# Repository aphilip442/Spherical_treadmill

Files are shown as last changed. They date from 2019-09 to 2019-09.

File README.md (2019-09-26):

# Spherical_treadmill

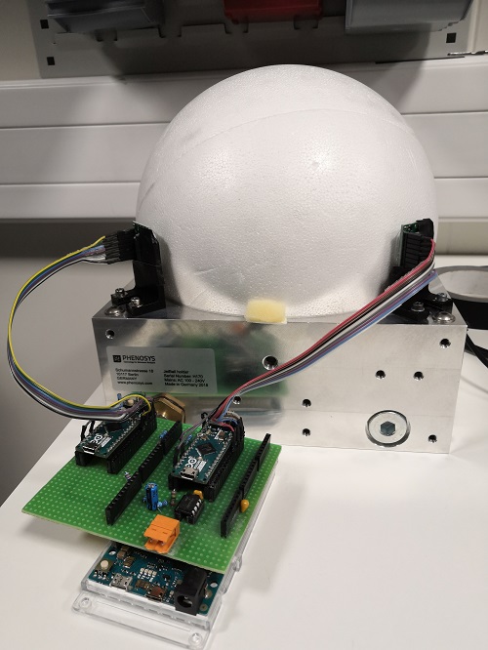
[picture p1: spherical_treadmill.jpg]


Mouse sensors and Arduinos to get the yaw-pitch-roll of an air-floating ball.

## Motivation

The ball and its holder (JetBall) are made by the company Phenosys. 

They also provide sensors that work similarly (mouse sensor + Arduino Micro) but are more limited (and compact, there is no Due) since they can only interface via USB, using 2 ports on the machine and requiring computations to take place on the PC.

Since our setups sometimes involve 1 PC for multiple rigs, it is easier to have one Arduino Due per setup and delegate computations.

Also, some of our original sensors broke: the company sells the sensors ~2600€ a pair, and the parts to make the full system from scratch cost ~100€ top.

## Setup

Two PMW3360 high-end gaming mouse sensors are used to track the XY displacement of a polystyrene ball (see picture). 

You can buy them here for 30$: https://www.tindie.com/products/jkicklighter/pmw3360-motion-sensor/

Those sensors are connected to Arduino Micro's (which you can buy in a variety of places for 20$). 

The full code for them  is available here: https://github.com/SunjunKim/PMW3360_Arduino

I use the PWM3360DM-Burst script, which is included in this repo.

Those Micro's are sending XY displacement to an Arduino Due, which computes the yaw-pitch-roll displacements of the ball.

From there other informations can be computed, like speed.

### Connections

Pinout Sensor-Micro:
* MI = MISO
* MO = MOSI
* SS = Slave Select / Chip Select
* SC = SPI Clock
* MT = Motion (active low interrupt line)
* RS = Reset
* GD = Ground
* VI = Voltage in up to +5.5V

Pinout Micro-Due:
* GND = GND
* Vin = 5V
* Tx = Rx2/Rx3 

WARNING: the Micro outputs 5V and the Due takes 3.3V, so don't forget to place a voltage divider in-between like follows:
  Micro Tx - 1k resistor - Due Rx - 2k resistor - GND

Note: the additional circuitry (see below) and 2-pin connector allows to send a 12V analog signal to a NIDAQ card. This implies using a 12V power supply for the Due (instead of 5V).
You should add a 10uF decoupling capacitor between the Vin and GND of your Due (as close as possible to the pins), and a 0.1uF decoupling capacitor between the Vin and GND of the LM358 (as close as possible to the pins).
This will result in a much cleaner output analog signal.

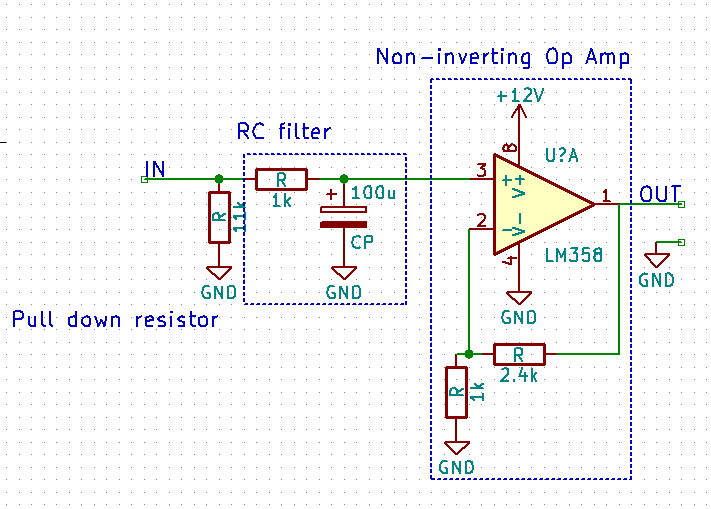
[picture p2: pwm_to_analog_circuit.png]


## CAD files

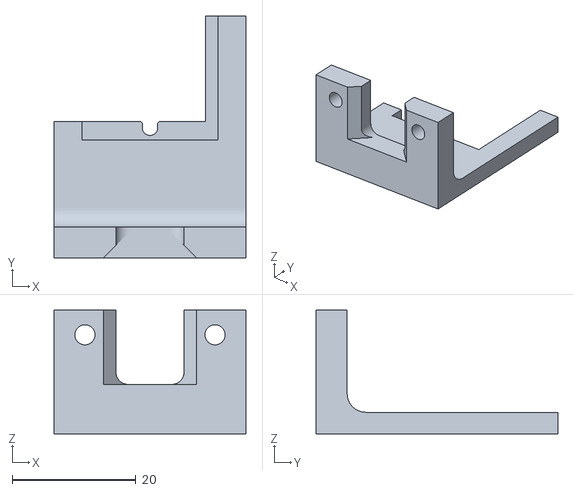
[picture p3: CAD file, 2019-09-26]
sensor_holder.STL
31.0 x 39.0 x 20.0

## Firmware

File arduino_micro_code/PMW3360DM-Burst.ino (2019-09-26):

#include <SPI.h>
#include <avr/pgmspace.h>

/*MIT License

Copyright (c) 2019 Sunjun Kim

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
THE SOFTWARE IS PROVIDED "AS IS", WITHOUT WARRANTY OF ANY KIND, EXPRESS OR
IMPLIED, INCLUDING BUT NOT LIMITED TO THE WARRANTIES OF MERCHANTABILITY,
FITNESS FOR A PARTICULAR PURPOSE AND NONINFRINGEMENT. IN NO EVENT SHALL THE
AUTHORS OR COPYRIGHT HOLDERS BE LIABLE FOR ANY CLAIM, DAMAGES OR OTHER
LIABILITY, WHETHER IN AN ACTION OF CONTRACT, TORT OR OTHERWISE, ARISING FROM,
OUT OF OR IN CONNECTION WITH THE SOFTWARE OR THE USE OR OTHER DEALINGS IN THE
SOFTWARE.*/


// Configurations
// The CPI value should be in between 100 -- 12000
#define CPI       1600

#define STX '@'
#define ETX '\n'
#define SEP '_'
unsigned long prev_time = 0;
#define TX_SERIAL 10
int x_serial = 0;
int y_serial = 0;

// Registers
#define Product_ID  0x00
#define Revision_ID 0x01
#define Motion  0x02
#define Delta_X_L 0x03
#define Delta_X_H 0x04
#define Delta_Y_L 0x05
#define Delta_Y_H 0x06
#define SQUAL 0x07
#define Raw_Data_Sum  0x08
#define Maximum_Raw_data  0x09
#define Minimum_Raw_data  0x0A
#define Shutter_Lower 0x0B
#define Shutter_Upper 0x0C
#define Control 0x0D
#define Config1 0x0F
#define Config2 0x10
#define Angle_Tune  0x11
#define Frame_Capture 0x12
#define SROM_Enable 0x13
#define Run_Downshift 0x14
#define Rest1_Rate_Lower  0x15
#define Rest1_Rate_Upper  0x16
#define Rest1_Downshift 0x17
#define Rest2_Rate_Lower  0x18
#define Rest2_Rate_Upper  0x19
#define Rest2_Downshift 0x1A
#define Rest3_Rate_Lower  0x1B
#define Rest3_Rate_Upper  0x1C
#define Observation 0x24
#define Data_Out_Lower  0x25
#define Data_Out_Upper  0x26
#define Raw_Data_Dump 0x29
#define SROM_ID 0x2A
#define Min_SQ_Run  0x2B
#define Raw_Data_Threshold  0x2C
#define Config5 0x2F
#define Power_Up_Reset  0x3A
#define Shutdown  0x3B
#define Inverse_Product_ID  0x3F
#define LiftCutoff_Tune3  0x41
#define Angle_Snap  0x42
#define LiftCutoff_Tune1  0x4A
#define Motion_Burst  0x50
#define LiftCutoff_Tune_Timeout 0x58
#define LiftCutoff_Tune_Min_Length  0x5A
#define SROM_Load_Burst 0x62
#define Lift_Config 0x63
#define Raw_Data_Burst  0x64
#define LiftCutoff_Tune2  0x65

const int ncs = 10;  // This is the SPI "slave select" pin that the sensor is hooked up to

byte initComplete = 0;
bool inBurst = false;

//Be sure to add the SROM file into this sketch via "Sketch->Add File"
extern const unsigned short firmware_length;
extern const unsigned char firmware_data[];

void setup() {
  Serial.begin(115200);
  Serial1.begin(115200);
  
  pinMode (ncs, OUTPUT);
  
  SPI.begin();
  SPI.setDataMode(SPI_MODE3);
  SPI.setBitOrder(MSBFIRST);
  //SPI.setClockDivider(4);
  Serial.println("ON");
  
  performStartup();

  delay(1000);

  //dispRegisters();
  initComplete = 9;
}

void adns_com_begin() {
  digitalWrite(ncs, LOW);
}

void adns_com_end() {
  digitalWrite(ncs, HIGH);
}

byte adns_read_reg(byte reg_addr) {
  adns_com_begin();

  // send adress of the register, with MSBit = 0 to indicate it's a read
  SPI.transfer(reg_addr & 0x7f );
  delayMicroseconds(35); // tSRAD
  // read data
  byte data = SPI.transfer(0);

  delayMicroseconds(1); // tSCLK-NCS for read operation is 120ns
  adns_com_end();
  delayMicroseconds(19); //  tSRW/tSRR (=20us) minus tSCLK-NCS

  return data;
}

void adns_write_reg(byte reg_addr, byte data) {
  adns_com_begin();

  //send adress of the register, with MSBit = 1 to indicate it's a write
  SPI.transfer(reg_addr | 0x80 );
  //sent data
  SPI.transfer(data);

  delayMicroseconds(20); // tSCLK-NCS for write operation
  adns_com_end();
  delayMicroseconds(100); // tSWW/tSWR (=120us) minus tSCLK-NCS. Could be shortened, but is looks like a safe lower bound
}

void adns_upload_firmware() {
  // send the firmware to the chip, cf p.18 of the datasheet
  Serial.println("Uploading firmware...");

  //Write 0 to Rest_En bit of Config2 register to disable Rest mode.
  adns_write_reg(Config2, 0x00);

  // write 0x1d in SROM_enable reg for initializing
  adns_write_reg(SROM_Enable, 0x1d);

  // wait for more than one frame period
  delay(10); // assume that the frame rate is as low as 100fps... even if it should never be that low

  // write 0x18 to SROM_enable to start SROM download
  adns_write_reg(SROM_Enable, 0x18);

  // write the SROM file (=firmware data)
  adns_com_begin();
  SPI.transfer(SROM_Load_Burst | 0x80); // write burst destination adress
  delayMicroseconds(15);

  // send all bytes of the firmware
  unsigned char c;
  for (int i = 0; i < firmware_length; i++) {
    c = (unsigned char)pgm_read_byte(firmware_data + i);
    SPI.transfer(c);
    delayMicroseconds(15);
  }

  //Read the SROM_ID register to verify the ID before any other register reads or writes.
  adns_read_reg(SROM_ID);

  //Write 0x00 to Config2 register for wired mouse or 0x20 for wireless mouse design.
  adns_write_reg(Config2, 0x00);

  adns_com_end();
}

void setCPI(int cpi)
{
  int cpival = constrain((cpi/100)-1, 0, 0x77); // limits to 0--119 

  adns_com_begin();
  adns_write_reg(Config1, cpival);
  adns_com_end();

  Serial.print("Set cpi to ");
  Serial.println(cpi);
}

void performStartup(void) {
  // hard reset
  adns_com_end(); // ensure that the serial port is reset
  adns_com_begin(); // ensure that the serial port is reset
  adns_com_end(); // ensure that the serial port is reset
  
  adns_write_reg(Shutdown, 0xb6); // Shutdown first
  delay(300);
  
  adns_com_begin(); // drop and raise ncs to reset spi port
  delayMicroseconds(40);
  adns_com_end();
  delayMicroseconds(40);
  
  adns_write_reg(Power_Up_Reset, 0x5a); // force reset
  delay(50); // wait for it to reboot
  
  // read registers 0x02 to 0x06 (and discard the data)
  adns_read_reg(Motion);
  adns_read_reg(Delta_X_L);
  adns_read_reg(Delta_X_H);
  adns_read_reg(Delta_Y_L);
  adns_read_reg(Delta_Y_H);
  // upload the firmware
  adns_upload_firmware();
  delay(10);

  setCPI(CPI);
  Serial.println("Optical Chip Initialized");
}

void dispRegisters(void) {
  int oreg[7] = {
    0x00, 0x3F, 0x2A, 0x02
  };
  char* oregname[] = {
    "Product_ID", "Inverse_Product_ID", "SROM_Version", "Motion"
  };
  byte regres;

  digitalWrite(ncs, LOW);

  int rctr = 0;
  for (rctr = 0; rctr < 4; rctr++) {
    SPI.transfer(oreg[rctr]);
    delay(1);
    Serial.println("---");
    Serial.println(oregname[rctr]);
    Serial.println(oreg[rctr], HEX);
    regres = SPI.transfer(0);
    Serial.println(regres, BIN);
    Serial.println(regres, HEX);
    delay(1);
  }
  digitalWrite(ncs, HIGH);
}

void loop() {
  byte burstBuffer[12];
  
  adns_com_begin();
  SPI.beginTransaction(SPISettings(4000000, MSBFIRST, SPI_MODE3));

  SPI.transfer(Motion_Burst);    
  delayMicroseconds(35); // waits for tSRAD

  SPI.transfer(burstBuffer, 12); // read burst buffer
  delayMicroseconds(1); // tSCLK-NCS for read operation is 120ns

  SPI.endTransaction();
  /*
  BYTE[00] = Motion    = if the 7th bit is 1, a motion is detected.
  BYTE[01] = Observation  
  BYTE[02] = Delta_X_L = dx (LSB)
  BYTE[03] = Delta_X_H = dx (MSB) 
  BYTE[04] = Delta_Y_L = dy (LSB)
  BYTE[05] = Delta_Y_H = dy (MSB)
  BYTE[06] = SQUAL     = Surface Quality register, max 0x80
                       - Number of features on the surface = SQUAL * 8
  BYTE[07] = Raw_Data_Sum   = It reports the upper byte of an 18‐bit counter which sums all 1296 raw data in the current frame;
                             * Avg value = Raw_Data_Sum * 1024 / 1296
  BYTE[08] = Maximum_Raw_Data  = Max raw data value in current frame, max=127
  BYTE[09] = Minimum_Raw_Data  = Min raw data value in current frame, max=127
  BYTE[10] = Shutter_Upper     = Shutter LSB
  BYTE[11] = Shutter_Lower     = Shutter MSB, Shutter = shutter is adjusted to keep the average raw data values within normal operating ranges
  */
  
  int motion = (burstBuffer[0] & 0x80) > 0;
  int xl = burstBuffer[2];
  int xh = burstBuffer[3];
  int yl = burstBuffer[4];
  int yh = burstBuffer[5];
  
  int x = xh<<8 | xl;
  int y = yh<<8 | yl;
    
  adns_com_end();

  // update only if a movement is detected.
  if(motion)
  {
    x_serial += x;
    y_serial += y;
  }

  unsigned long time = millis();
  if (time - prev_time >= TX_SERIAL){
    Serial.print(STX);
    Serial.print(x_serial);
    Serial.print(SEP);
    Serial.print(y_serial);
    Serial.print(ETX);
    Serial1.print(STX);
    Serial1.print(x_serial);
    Serial1.print(SEP);
    Serial1.print(y_serial);
    Serial1.print(ETX);
    x_serial = 0;
    y_serial = 0;
    prev_time = time;
  }
  // limits the read rate
  delayMicroseconds(800);
}

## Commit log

2019-09-26 Upload arduino codes
2019-09-26 Added sensor holder STL file for 3D printing
    [sensor_holder.STL]
2019-09-26 Added PWM to analog circuit picture
2019-09-26 Added pwm to analog circuit
2019-09-26 Note about decoupling capacitors
